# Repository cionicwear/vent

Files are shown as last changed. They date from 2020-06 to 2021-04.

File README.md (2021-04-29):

# vent

Vent is a collaboration between CIONIC and FuseProject to build a highly modular low cost ventilator 
to help address a potential capacity shortfall in emergency COVID-19 response.

Our design is a finalist in the [Covent-19 Challenge](https://www.coventchallenge.com/)

## pi development

The fully featured Vent has been tested to run on [Raspberry Pi 4](https://www.raspberrypi.org/products/raspberry-pi-4-model-b/) 

The headless version has been tested to run on [Raspberry Pi 0](https://www.raspberrypi.org/products/raspberry-pi-zero-w/)

### pi setup

```
git clone https://github.com/cionicwear/vent.git
cd vent
sudo pip3 install -r requirements.txt
```

Vent requires running two i2c busses to configure your pi
Add the following overlay to /boot/config.txt
```
dtoverlay=i2c-gpio,i2c_gpio_sda=4,i2c_gpio_scl=26,bus=3
```

### pi running

There are three different processes that need to be 

1. start the ui process
```
sudo ./ui.py
```
The UI process manages the rotary encoder and buttons translating them to system wide keystrokes

2. start the vent process
```
sudo ./vent.py
```
The vent process is the primary control point that manges the web server, sensors, and valve.

3. start the screen process
```
./vent.sh
```
The chromium browser serves as the surface for operator input and display of sensor values

## desktop development

In order to enable hardware free development the vent can be run locally via docker.
```
git clone https://github.com/cionicwear/vent.git
cd vent
docker-compose up
```

## command line testing

Much of the vent functionality can be tested via the command line.  

```
sudo ./vent.py -h
```

will print out diffrent vent parameters that can be tested

```
usage: vent.py [-h] [-m MODE] [-a ASSIST] [-i INSPIRE] [-e EXPIRE] [-u RAMPUP]
               [-d RAMPDN] [-s START] [-t TOP] [-p PAUSE] [-b BOTTOM]
               [-c COUNT] [-f FIO2] [-v VTIDAL] [-w PWAIT] [-x PCROSS]

Run vent

optional arguments:
  -h, --help            show this help message and exit
  -m MODE, --mode MODE  0 = Demo 1 = Volume Control 2 = Pressure Control
  -a ASSIST, --assist ASSIST
                        pressure trigger for assist 0 = no assist
  -i INSPIRE, --inspire INSPIRE
                        seconds of inspiration time
  -e EXPIRE, --expire EXPIRE
                        seconds of expiration time
  -u RAMPUP, --rampup RAMPUP
                        seconds to ramp from <start> to <top>
  -d RAMPDN, --rampdn RAMPDN
                        seconds to ramp from <top> to <pause>
  -s START, --start START
                        percent open at start of breathing cycle
  -t TOP, --top TOP     percent open at peak of breathing cycle
  -p PAUSE, --pause PAUSE
                        percent open at pause in breathing cycle
  -b BOTTOM, --bottom BOTTOM
                        percent open at end of breathing cycle
  -c COUNT, --count COUNT
                        number of breathing cycles
  -f FIO2, --fio2 FIO2  fio2
  -v VTIDAL, --vtidal VTIDAL
                        tidal volume
  -w PWAIT, --pwait PWAIT
                        seconds to wait before closing peep
  -x PCROSS, --pcross PCROSS
                        peep crossing threshold
```

For example if you wanted to test
 - 1 second of inspire time
 - 90% air flow
 - with a 0.2 second peep time
 - for 10 cycles

You would run the command

```
sudo ./vent.py -c 10 -t 90 -w 0.2 -x 0.1
```

Note: the `-x -1` sets the peep pressure threshold to -1 to set the auto peep to trigger at -1 cmH20.  This is useful when testing the system with no airflow.

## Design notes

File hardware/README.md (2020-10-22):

# Hardware Specifications

There have been two revisions to the hardware reference design

* RevA initial concept
* RevB functional prototype

## RevB Functional Prototype

The RevB reference design made rapid deployment even easier by leveraging off the shelf breakout boards for almost all components.

[Mechanical Assembly](mechanical/RevB.STEP)

[Electrical Schematic](electrical/RevB.pdf)

[Bill of Materials](bom/RevB.csv)

Electronics

- 1x [Raspberry Pi 4](https://www.raspberrypi.org/products/raspberry-pi-4-model-b/) for compute
- 1x [Raspberry Pi Touch Display](https://www.raspberrypi.org/products/raspberry-pi-touch-display/) for UI
- 4x [Adafruit LPS33HW Pressure Sensor](https://www.adafruit.com/product/4414) for measuring pressure and flow
- 1x [Adafruit Motor Bonnet](https://www.adafruit.com/product/4280) for driving solenoids and linear actuator
- 2x [SMC PVQ31-6G-40-01-N Solenoid](https://www.smcpneumatics.com/pdfs/PVQ.pdf) for control of O2 and Room Air
- 1x [Actuonix L12-10-50-12-P Linear Actuator](https://s3.amazonaws.com/actuonix/Actuonix+L12+Datasheet.pdf) for controlling PEEP
- 1x [Sensoronics SS-26 O2 Sensor](https://www.sensoronics.com/products/ss-26-replaces-msa-806572) for O2 Sensing
- 1x [Sparkfun QWIIC ADS1105](https://www.sparkfun.com/products/15334) to read analog O2 and actuator position sensors
- 1x [GOOLOO GP37-plus](http://www.gooloo.com/products-detail.php?ProId=41) for power management and battery backup
- 2x [B3F-1020 Tactile Switch](https://www.digikey.com/product-detail/en/omron-electronics-inc-emc-div/B3F-1020/SW402-ND/44059) for UI
- 1x [PEC11R-4015F-S0024 Rotary Encoder](https://www.digikey.com/product-detail/en/bourns-inc/PEC11R-4015F-S0024/PEC11R-4015F-S0024-ND/4499668) for UI
- 1x [CEM-1203_42 Audio Transducer](https://www.digikey.com/product-detail/en/cui-devices/CEM-1203-42/102-1153-ND/412412) for Alarms

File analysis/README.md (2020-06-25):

## FMEA

The team conducted a [Failure Mode and Effects Analysis](https://github.com/cionicwear/vent/blob/master/analysis/VOX_FMEA.xlsx) to determine areas of risk with this reference design

## Ventilator Mode Testing

Ventilator modes  tested using refrence equipment from AD Instruments and MGH/Ximedica (listed in table below)  
That data was then exported for anlysis vs. system diagnostics generated by the VOX vent  
And compared in Jupyter notebooks [vent.ipynb](analysis/vent.ipynb) to generate pdf reports (linked in table below)

|   Pressure Transducer                                |   ADInstruments   |   Measure the air pressure.                                                     | Tidal Volume ml | Breaths / min (a) | Inspire time (s) | O2 | BAP (PEEP) | I:E |
|------------------------------------------------------|-------------------|---------------------------------------------------------------------------------|-----------------|-------------------|------------------|----|------------|-----|
|   FE221 Bridge Amp                                   |   ADInstruments   |   Sends data from pressure transducer to PowerLab.                              | 500             | 20                | 1                | 30 | 5          | 1:2 |
|   Cables                                             |   ADInstruments   |   Used to connect amp to PowerLab.                                              | 500             | 12                | 1                | 90 | 10         | 1:4 |
|   MLT1000 Flow Head                                  |   ADInstruments   |   Used to measure air flow.                                                     | 500             | 20                | 1                | 90 | 5          | 1:2 |
|   Flow Head Tubing                                   |   ADInstruments   |   Connects between flow head and spirometer.                                    | 500             | 20                | 1                | 30 | 10         |     |
|   ML311 Spirometer Pod                               |   ADInstruments   |   Measures the flow rate of air for other calculations.                         | 300             | 20                | 1                | 30 | 5          |     |
|   PowerLab                                           |   ADInstruments   |   Collects data and sends to LabChart.                                          | 300             | 12                | 1                | 90 | 10         | 1:3 |
|   LabChart License                                   |   ADInstruments   |   Used to collect, display, and analyze data.                                   | 300             | 20                | 1                | 30 | 10         |     |
|   IngMar Medical QuickLung Test Lung or Equivalent   |   MGH/Ximedica    |   Has adjustable resistance and compliance to help simulate a person’s lungs.   | 200             | 20                | 1                | 90 | 5          |     |

### Pressure Control Testing

|   | Compliance ml/hPa ±10%                                                       | Resistance  hPa/l/s ±10% | Tidal Volume ml (a) | Breaths / min (b) | Inspire time (s) (c) | O2 | BAP (PEEP) | Δ insp pressure (d) |
|---|------------------------------------------------------------------------------|--------------------------|---------------------|-------------------|----------------------|----|------------|---------------------|
| [ISO_PCV1](ISO_PCV1.pdf) | 50.                                                            | 5                        | 500                 | 20                | 1                    | 30 | 5          | 10                  |
| [ISO_PCV2](ISO_PCV2.pdf) | 50                                                                           | 20                       | 500                 | 12                | 1                    | 90 | 10         | 15                  |                                     |
| ISO_PCV3 | 20                                                                           | 5                        | 500                 | 20                | 1                    | 90 | 5          | 25                  |

### Volume Control Testing

|      | Compliance ml/hPa ±10% | Resistance  hPa/l/s ±10% | Tidal Volume ml | Breaths / min (a) | Inspire time (s) | O2 | BAP (PEEP) | I:E |
|------|------------------------|--------------------------|-----------------|-------------------|------------------|----|------------|-----|
| [ISO1](ISO1.pdf)    | 50                     | 5                        | 500             | 20                | 1                | 30 | 5          | 1:2 |
| [ISO2](ISO2.pdf)   | 50                     | 20                       | 500             | 12                | 1                | 90 | 10         | 1:4 |
| [ISO3](ISO3.pdf)   | 20                     | 5                        | 500             | 20                | 1                | 90 | 5          | 1:2 |
| 4    | 20                     | 20                       | 500             | 20                | 1                | 30 | 10         |     |
| 5    | 20                     | 20                       | 300             | 20                | 1                | 30 | 5          |     |
| 6    | 20                     | 50                       | 300             | 12                | 1                | 90 | 10         | 1:3 |
| 7    | 10                     | 50                       | 300             | 20                | 1                | 30 | 10         |     |
| 8    | 10                     | 10                       | 200             | 20                | 1                | 90 | 5          |     |
| [C200](C200.pdf)  | 50                     | 5                        | 200             | 15                | 1                | 20 | 5          | 1:3 |
| C300 | 50                     | 5                        | 300             | 15                | 1                | 20 | 5          | 1:3 |
| C400 | 50                     | 5                        | 400             | 15                | 1                | 20 | 5          | 1:3 |
| C500 | 50                     | 5                        | 500             | 15                | 1                | 20 | 5          | 1:3 |
| C600 | 50                     | 5                        | 600             | 15                | 1                | 20 | 5          | 1:3 |
| [P15](P15.pdf)  | 50                     | 5                        | 500             | 10                | 1                | 20 | 15         | 1:5 |
| [R30](R30.pdf)  | 50                     | 5                        | 200             | 30                | 1                | 20 | 5          | 1:1 |

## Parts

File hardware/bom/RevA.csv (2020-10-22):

QTY | Description | P/N
6 | SCREW M3 x 5mm BH TORX | 92832A214
1 | RELIEF VALVE | 48935K250
2 | VENTURI TUBE ELBOW ADAPTER | PRINTED
1 | VENTURI TUBE EXHALE | PRINTED
1 | BARREL JACK 2.1mm DC | 610 ADAFRUIT
1 | COVER PANEL REAR | MACHINED
6 | SCREW M5 x 8mm PH TORX | 90304A218
8 | SCREW M4 x 8mm FH THREAD FORMING | STP41040-0080
1 | O2 SENSOR | SS-26
1 | VENTURI TUBE ADAPTER | PRINTED
1 | VENTURI TUBE INHALE | PRINTED
1 | ROTARY ENCODER | PEC11R-4015F-S0024
1 | POWER BUTTON | IPR1SAD2
1 | ENCLOSURE | PRINTED
4 | SCREW M3 x 12mm PH THREAD FORMING | 96817A912
2 | QUICK DISCONNECT AIR CONNECT ADAPTER | 5012K320
1 | HIGH-PURITY POLYPROPYLENE TUBING 0.25 INCH OD | 4218N11
1 | HIGH-PURITY POLYPROPYLENE TUBING 0.25 INCH OD | 4218N11
1 | HIGH-PURITY POLYPROPYLENE TUBING 0.25 INCH OD | 4218N11
1 | HIGH-PURITY POLYPROPYLENE TUBING 0.25 INCH OD | 4218N11
1 | HIGH-PURITY POLYPROPYLENE TUBING 0.25 INCH OD | 4218N11
1 | HIGH-PURITY POLYPROPYLENE TUBING 0.25 INCH OD | 4218N11
1 | HIGH-PURITY POLYPROPYLENE TUBING 0.25 INCH OD | 4218N11
1 | HIGH-PURITY POLYPROPYLENE TUBING 0.25 INCH OD | 4218N11
1 | HIGH-PURITY POLYPROPYLENE TUBING 0.25 INCH OD | 4218N11
1 | HIGH-PURITY POLYPROPYLENE TUBING 0.25 INCH OD | 4218N11
1 | HIGH-PURITY POLYPROPYLENE TUBING 0.25 INCH OD | 4218N11
1 | SUB-ASSY VALVE PLATE | 3D printed
3 | FITTING AIR MALE-PUSH CONNECT 0.125 INCH NPT | KQ2H07-34N
1 | RASPBERRY PI 4 MODEL B | RPI4B
6 | SCREW M2.63 x 5mm RH TORX THREAD FORMING | 99397A413
1 | HIGH-PURITY HARD POLYPROPYLENE TUBING | 4218N11
4 | FITTING AIR MALE-PUSH CONNECT 0.25 INCH NPT | KQ2H07-35N
3 | PROPORTIONAL SOLENOID VALVE | PVQ31-6G-16-01-F
2 | METRIC THREAD-FORMING SCREW FOR PLASTIC | 99397A679
1 | REGULATOR BRACKET | -
1 | PUSH-CONNECT BRANCH TEE TUBING ADAPTER | KQ2T07-34AS
1 | HIGH-PURITY HARD POLYPROPYLENE TUBING | 4218N11
2 | NONADJUSTABLE MINIATURE AIR WATER REGULATOR | 9386K410
2 | CHECK VALVE | AKH07B-N01S
1 | SENSOR BOARD PCBA | -
2 | DIFFERENTIAL PRESSURE SENSOR | D6F_P0010A2
1 | SENSOR BOARD PCB | -
2 | PRESURE SENSOR GAUGE | P-2000-501G-15-BN
4 | SCREW M2.63 x 8mm RH TORX THREAD FORMING | 99397A415
1 | HIGH-PURITY HARD POLYPROPYLENE TUBING | 4218N11
1 | PLATE ABS VALVE MOUNTING | -
1 | BRACKET CABLE MANAGEMENT | -
1 | PEEP VALVE | -
1 | SUB-ASSY FRONT PLATE | MACHINED
1 | COVER PANEL FRONT | MACHINED
6 | STAINLESS STEEL STAND-OFF | CSS-M3-12
1 | SUB-ASSY DISPLAY | -
10 | SCREW M2.63 x 8mm RH TORX THREAD FORMING | 99397A415
1 | DISPLAY MOUNT | PRINTED
1 | RASPBERRY PI 7IN LCD | 8997466
1 | BUTTON PCBA | -
2 | TACTILE SWITCH SPST-NO | B3F-1020
1 | MAGNETIC BUZZER TRANSDUCER | CEM-1203_42
1 | BUTTON PCB | -
4 | SCREW M3 x 5mm PH PHILLIPS | 90116A150
2 | BUTTON COVER COSMETIC | PRINTED
1 | PI DISPLAY PCBA | -
3 | IV POLE C-CLAMP | BK-IVP-8950
1 | TUBE GUIDE PATIENT CIRCUIT | -
1 | Quad Low-Side Solenoid Driver | DRV8803
1 | Power Management IC | TPS259571DSGR
1 | Analog to Digital Converter | ADS1115IDGSR

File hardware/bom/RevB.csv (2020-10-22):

QTY | Description | P/N
PRINTED
1 | ENCLOSURE | PRINTED
1 | LINEAR ACTUATOR MOUNT | PRINTED
1 | VALVE MOUNTING PLATE | PRINTED
1 | BRACKET CABLE MANAGEMENT | PRINTED
1 | DISPLAY MOUNT | PRINTED
1 | VENTURI INSPIRATION | PRINTED
1 | VENTURI EXPIRATION | PRINTED
2 | BUTTON COVER COSMETIC | PRINTED
1 | ROTARY ENCODER COVER COSMETIC | PRINTED
1 | LINEAR ACTUATOR PEEP CAP | PRINTED
1 | OXYGEN SENSOR MOUNT | PRINTED
MACHINED
1 | FRONT COVER PANEL WITH STANDOFFS | MACHINED
1 | TUBE GUIDE PATIENT CIRCUIT | MACHINED
1 | REAR COVER PANEL | MACHINED
ELECTRONICS
1 | OXYGEN SENSOR | SENSORONICS SS26
2 | PROPORTIONAL SOLENOID VALVE | SMC PVQ31-6G-40-01N
1 | LINEAR ACTUATOR | ACTUONIX L12-10-50-12-P
1 | RASPBERRY PI 7IN LCD | DIGIKEY 1690-1007-ND
1 | RASPBERRY PI 4 MODEL B | DIGIKEY 1690-RASPBERRYPI4B/2GB-ND
1 | ADAFRUIT MOTOR BONNET 4280 | DIGIKEY 1528-4280-ND
4 | PRESSURE SENSOR LPS33HW BREAKOUT 4414 | DIGIKEY 1528-4414-ND
1 | BATTERY BACKUP | GOOLOO GP37+
1 | MAGNETIC BUZZER TRANSDUCER CEM-1203(42) | DIGIKEY 102-1153-ND
2 | TACTILE SWITCH B3F-1020 | DIGIKEY SW402-ND
1 | ADAFRUIT PANEL MOUNT BARREL JACK 2.1mm DC | ADAFRUIT 610
1 | ROTARY ENCODER | DIGIKEY PEC11R-4015F-S0024-ND
1 | PANEL MOUNT POWER BUTTON IPR1SAD2 | DIGIKEY 679-1099-ND
1 | SPARKFUN QWIIC ADS1015 BREAKOUT | DIGIKEY 1568-DEV-15334-ND
1 | BUTTON PCBA | HAND SOLDERED
OTHER
3 | IV POLE C-CLAMP | BK-IVP-8950
1 | 70A BUNA N 001-1/2 O RING (100 pack) | MCMASTER 9452K311
2 | QUICK DISCONNECT AIR CONNECT ADAPTER | MCMASTER 5012K44
2 | QUICK DISCONNECT AIR CONNECT ADAPTER | MCMASTER 5012K34
1 | HIGH-PURITY POLYPROPYLENE TUBING 1/4 IN OD | MCMASTER 4218N11
1 | HIGH-PURITY POLYPROPYLENE TUBING 3/8 IN OD | MCMASTER 4218N12
1 | PUSH TO CONNECT WYE 3/8 IN OD | MCMASTER 5779K46
5 | PUSH TO CONNECT TUBE FITTING 3/8 IN OD 1/8 NPT | MCMASTER 5779K115
2 | PUSH TO CONNECT TUBE FITTING 1/4 IN OD 1/8 NPT | MCMASTER 5779K108
1 | PRESSURE RELIEF VALVE | 48935K250
10 | SCREW M2.63 x 8mm RH TORX THREAD FORMING | 99397A415
4 | SCREW M3 x 5mm PH PHILLIPS | 90116A150
6 | SCREW M2.63 x 5mm RH TORX THREAD FORMING | 99397A413
4 | SCREW M3 x 12mm PH THREAD FORMING | 96817A912
6 | SCREW M5 x 8mm PH TORX | 90304A218
8 | SCREW M4 x 8mm FH THREAD FORMING | STP41040-0080
1 | LINEAR ACTUATOR PEEP CAP PADDING | TBD

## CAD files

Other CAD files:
hardware/mechanical/RevA.STEP
hardware/mechanical/RevB.STEP

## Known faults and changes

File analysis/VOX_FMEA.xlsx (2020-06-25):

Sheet: FMEA
Product/Process | InVent Ventilator | Date Created | 2020-05-08
Prepared By | Jonathan Schreven & Eric Spaulding
Notes | Last updated on 5/11/2020 by Jonathan Schreven
Function / Requirement | Potential failure mode | Potential effect of failure | SEV | Class | Current process controls |  |  |  |  |  | Recommended actions |  |  | Action results
 |  |  |  |  | Potential cause | Occur | Prevention | Detection | Det | R.P.N. | Recommended actions | Responsible | Target completion date | Actions Taken | Sev | Occur | Det | R.P.N. | Class
O2 Inlet Fitting | Air supply line connected | Incorrect FiO2 delivery to patient | 8 |  | User error | 5 | None | Visual inspection, FiO2 alarm | 5 | 200 |  |  |  |  |  |  |  | 0
 | External O2 line disconnects | Incorrect/insufficient O2 delivery to patient | 6 |  | Connector breaks | 1 | Locking connector | Visual inspection | 2 | 12 |  |  |  |  |  |  |  | 0
 | Internal tubing disconnects | Incorrect/insufficient O2 delivery to patient | 6 |  | Tube slips off fitting | 1 | Multi-barbed fitting | Audible gas leak | 2 | 12 |  |  |  |  |  |  |  | 0
 | Insufficient inlet pressure | Insufficient outlet pressure to drive patient breath | 5 |  | Tank empty or nearly empty | 8 | None | FiO2 alarm | 2 | 80 |  |  |  |  |  |  |  | 0
 |  |  |  |  | Incorrect O2 tank pressure setting | 8 | None | FiO2 alarm | 3 | 120 |  |  |  |  |  |  |  | 0
 |  |  |  |  |  |  |  |  |  | 0 |  |  |  |  |  |  |  | 0
O2 Inlet Pressure Regulator | Pressure setting too low | Incorrect FiO2 delivery to patient | 5 |  | Manufacturer quality control issue | 1 | None | FiO2 alarm | 1 | 5 |  |  |  |  |  |  |  | 0
 | Pressure setting too high | Damage air mixing tank structure | 5 |  | Manufacturer quality control issue | 1 | None | FiO2 Alarm, Audible gas leak | 7 | 35 |  |  |  |  |  |  |  | 0
 | Tubing disconnect | Incorrect FiO2 delivery to patient | 6 |  | Improper assembly | 2 | None | FiO2 Alarm, Audible gas leak | 2 | 24 |  |  |  |  |  |  |  | 0
 |  |  |  |  |  |  |  |  |  | 0 |  |  |  |  |  |  |  | 0
O2 Inlet Solenoid | Power Failure | N.C. Valve - Oxygen line turns off | 6 |  | Power cord removed from wall/unit | 3 | Cable management | Visual inspection | 1 | 18 |  |  |  |  |  |  |  | 0
 |  |  |  |  | Bump power switch | 5 | Flush button on rear of unit | Visual inspection | 3 | 90 |  |  |  |  |  |  |  | 0
 | Tubing disconnect | Incorrect FiO2 delivery to patient | 6 |  | Improper assembly | 2 | None | Audible gas leak, FiO2 alarm | 2 | 24 |  |  |  |  |  |  |  | 0
 | Seal fails | Incorrect FiO2 delivery to patient | 5 |  | Manufacturer defect | 1 | None | Audible gas leak, FiO2 alarm | 3 | 15 |  |  |  |  |  |  |  | 0
 |  |  |  |  |  |  |  |  |  | 0 |  |  |  |  |  |  |  | 0
Air Inlet Fitting | O2 supply line connected | Incorrect FiO2 delivery to patient | 8 |  | User error | 5 | None | Visual inspection, FiO2 alarm | 5 | 200 |  |  |  |  |  |  |  | 0
 | External Air line disconnects | Incorrect/insufficient O2 delivery to patient | 8 |  | Connector breaks | 1 | Locking connector | Visual inspection | 2 | 16 |  |  |  |  |  |  |  | 0
 | Internal tubing disconnects | Incorrect/insufficient O2 delivery to patient | 8 |  | Tube slips off fitting | 1 | Barbed fitting | Audible gas leak | 2 | 16 |  |  |  |  |  |  |  | 0
 | Insufficient inlet pressure | Insufficient outlet pressure to drive patient breath | 5 |  | Tank empty or nearly empty | 8 | None | FiO2 alarm | 2 | 80 |  |  |  |  |  |  |  | 0
 |  |  |  |  | Incorrect O2 tank pressure setting | 8 | None | FiO2 alarm | 3 | 120 |  |  |  |  |  |  |  | 0
 |  |  |  |  |  |  |  |  |  | 0 |  |  |  |  |  |  |  | 0
Air Inlet Pressure Regulator | Pressure setting too low | Incorrect FiO2 delivery to patient | 5 |  | Manufacturer quality control issue | 1 | None | FiO2 alarm | 1 | 5 |  |  |  |  |  |  |  | 0
 | Pressure setting too high | Damage air mixing tank | 5 |  | Manufacturer quality control issue | 1 | None | FiO2 Alarm, Audible gas leak | 7 | 35 |  |  |  |  |  |  |  | 0
 | Tubing disconnect | Incorrect FiO2 delivery to patient | 8 |  | Improper assembly | 2 | None | FiO2 Alarm, Audible gas leak | 2 | 32 |  |  |  |  |  |  |  | 0
 |  |  |  |  |  |  |  |  |  | 0 |  |  |  |  |  |  |  | 0
Air Inlet Solenoid | Power Failure | N.C. Valve - Air line turns off | 8 |  | Power cord removed from wall/unit | 3 | Cable management | Visual inspection | 1 | 24 |  |  |  |  |  |  |  | 0
 |  |  |  |  | Bump power switch | 5 | Flush button on rear of unit | Visual inspection | 3 | 120 |  |  |  |  |  |  |  | 0
 | Tubing disconnect | Incorrect FiO2 delivery to patient | 8 |  | Improper assembly | 2 | None | Audible gas leak, FiO2 alarm | 2 | 32 |  |  |  |  |  |  |  | 0
 | Seal fails | Incorrect FiO2 delivery to patient | 7 |  | Manufacturer defect | 1 | None | Audible gas leak, FiO2 alarm | 3 | 21 |  |  |  |  |  |  |  | 0
 |  |  |  |  |  |  |  |  |  | 0 |  |  |  |  |  |  |  | 0
Gas Mixing Tank | Hose barb breaks | No gas delivery to patient | 9 |  | Fatigue from hose movement | 3 | Functional prototype cycle testing | Audible gas leak, FiO2 alarm | 2 | 54 |  |  |  |  |  |  |  | 0
 | Tank damage | No gas to patient | 10 |  | Over pressure | 2 | FEA Analysis, SF = 3 | Audible gas leak, FiO2 alarm | 2 | 40 |  |  |  |  |  |  |  | 0
 | Tank gasket fails | Insufficient outlet pressure to drive patient breath | 8 |  | Assembly error | 3 | Pressure check at manufacturing | Audible gas leak, FiO2 alarm | 3 | 72 |  |  |  |  |  |  |  | 0
 |  |  |  |  | System Overpressure | 1 | Upstream pressure regulators | Audible gas leak, FiO2 alarm | 3 | 24 |  |  |  |  |  |  |  | 0
 | Tubing disconnect | No gas to patient | 9 |  | Tube slips off fitting | 2 | Barbed fitting | Audible gas leak | 3 | 54 |  |  |  |  |  |  |  | 0
 |  |  |  |  |  |  |  |  |  | 0 |  |  |  |  |  |  |  | 0
Gas Outlet Solenoid | Power Failure | N.C. Valve - No gas to patient | 9 |  | Power cord removed from wall/unit | 3 | Cable management | Visual inspection | 1 | 27 |  |  |  |  |  |  |  | 0
 |  |  |  |  | Bump power switch | 5 | Flush button on rear of unit | Visual inspection | 3 | 135 |  |  |  |  |  |  |  | 0
 | Tubing disconnect | Incorrect FiO2 delivery to patient | 9 |  | Improper assembly | 2 | None | Audible gas leak, FiO2 alarm | 2 | 36 |  |  |  |  |  |  |  | 0
 | Seal fails | Incorrect FiO2 delivery to patient | 7 |  | Manufacturer defect | 1 | None | Audible gas leak, FiO2 alarm | 3 | 21 |  |  |  |  |  |  |  | 0
 | Valve sticks open | Excessive pressure delivered to patient | 9 |  | Mechanical valve failure | 2 | Emergency pressure relief valve | PIP monitor | 1 | 18 |  |  |  |  |  |  |  | 0
 |  |  |  |  | Erroneous control system signal | 2 | System testing, emergency pressure relief valve | PIP monitor | 1 | 18 |  |  |  |  |  |  |  | 0
 | Valve doesn't open enough | Insufficient air volume/flow rate to patient | 8 |  | Erroneous control system signal | 2 | System testing | Tidal Volume not achieved alarm | 1 | 16 |  |  |  |  |  |  |  | 0
 |  |  |  |  |  |  |  |  |  | 0 |  |  |  |  |  |  |  | 0
Inspiratory Flow Sensor (Venturi) | Sensor tubing disconnects | Incorrect gas delivery to patient | 9 |  | Improper assembly | 2 | Pressure check at manufacturing | Tidal Volume not achieved alarm | 3 | 54 | System pause for suspected sensor failure |  |  |  |  |  |  | 0
 | Hose disconnects | No gas delivery to patient | 9 |  | Tube slips off fitting | 2 | Barbed fitting | Audible gas leak | 3 | 54 |  |  |  |  |  |  |  | 0
 | Inlet hose barb breaks | No gas delivery to patient | 9 |  | Fatigue from hose movement | 3 | Functional prototype cycle testing | Audible gas leak, FiO2 alarm | 2 | 54 |  |  |  |  |  |  |  | 0
 | Sensor barb breaks | Incorrect tidal volume to patient | 10 |  | Fatigue from hose movement | 3 | Functional prototype cycle testing | Audible gas leak, FiO2 alarm | 2 | 60 | NPT barbs? |  |  |  |  |  |  | 0
 | Incorrect flow measure | Incorrect tidal volume to patient | 10 |  | Differential pressure sensor malfunction | 2 | Testing against calibrated flow sensor | Tidal volume not achieved alarm | 2 | 40 |  |  |  |  |  |  |  | 0
 | Incorrect pressure measurement | Excess pressure to patient | 9 |  | Pressure sensor malfunction | 2 | None | Insp. Pressure not achieved alarm | 4 | 72 |  |  |  |  |  |  |  | 0
 | Incorrect pressure measurement | Insufficient pressure to patient | 9 |  | Pressure sensor malfunction | 2 | None | Insp. Pressure not achieved alarm | 4 | 72 |  |  |  |  |  |  |  | 0
 |  |  |  |  |  |  |  |  |  | 0 |  |  |  |  |  |  |  | 0
Inspiratory Hose Connection | Hose disconnects | No delivery to paitient | 9 |  | Hose gets caught on something/someone | 3 | Designed to ISO standard, vertical port orientation | External patient sensors (e.g. pulse ox.) | 5 | 135 |  |  |  |  |  |  |  | 0
 | Connection breaks | Incorrect patient gas delivery | 9 |  | Unit dropped | 2 | Designed to ISO standard, port protected behind display | Insp. Pressure and Tidal volume not achieved alarms | 4 | 72 |  |  |  |  |  |  |  | 0
 |  |  |  |  |  |  |  |  |  | 0 |  |  |  |  |  |  |  | 0
Expiratory Hose Connection | Hose disconnects | Incorrect expiratory pressure | 8 |  | Hose gets caught on something/someone | 3 | Designed to ISO standard, vertical port orientation | External patient sensors (e.g. pulse ox.) | 5 | 120 |  |  |  |  |  |  |  | 0
 | Connection breaks | Incorrect patient gas delivery | 8 |  | Unit dropped | 2 | Designed to ISO standard, port protected behind display | Insp. Pressure and Tidal volume not achieved alarms | 4 | 64 |  |  |  |  |  |  |  | 0
 |  |  |  |  |  |  |  |  |  | 0 |  |  |  |  |  |  |  | 0
Expiratory Flow Sensor (Venturi) | Sensor tubing disconnects | Sensors produce false data | 8 |  | Improper assembly | 2 | Pressure check at manufacturing | Tidal Volume not achieved alarm | 3 | 48 |  |  |  |  |  |  |  | 0
 | Hose disconnects | Unable to measure expiratory flow and pressure | 8 |  | Tube slips off fitting | 2 | Barbed fitting | Audible gas leak | 3 | 48 |  |  |  |  |  |  |  | 0
 | Incorrect flow measure | Incorrect measure of patient breating status | 6 |  | Differential pressure sensor malfunction | 2 | Testing against calibrated flow sensor | Tidal volume not achieved alarm | 2 | 24 |  |  |  |  |  |  |  | 0
 | Incorrect PEEP measurement | Incorrect data output | 4 |  | Pressure sensor malfunction | 2 | None | Insp. Pressure not achieved alarm | 4 | 32 |  |  |  |  |  |  |  | 0
 |  |  |  |  |  |  |  |  |  | 0 |  |  |  |  |  |  |  | 0
Unit Mounting | Ventilator slides down IV pole | Patient circuit and/or power disconnect | 9 |  | Pole clamps not tightened enough | 2 | None | Visual observation | 4 | 72 |  |  |  |  |  |  |  | 0
 |  |  |  |  | Bolt loosens due to vibration while moving | 2 | None | Visual observation | 4 | 72 |  |  |  |  |  |  |  | 0
 |  |  |  |  |  |  |  |  |  | 0 |  |  |  |  |  |  |  | 0
Oxygen Sensor | Sensor Failure | Incorrect FiO2 delivery to patient | 9 |  | Fails with normal reading | 2 | None | None | 10 | 180 |  |  |  |  |  |  |  | 0
 |  |  |  |  | Fails with extreme value | 2 | None | Insp. Pressure not achieved or overpressure alarm | 2 | 36 |  |  |  |  |  |  |  | 0
 | Oring failure | Insufficient outlet pressure to drive patient breath | 8 |  | Over compression of o-ring | 2 | None | Audible gas leak, tidal volume and insp. Pressure not achieved alarms | 2 | 32 |  |  |  |  |  |  |  | 0
 | Incorrect characterization of FiO2 in tank | Incorrect FiO2 delivery to patient | 10 |  | Incorrect tank mixing properties | 4 | Testing against calibrated O2 sensor | Visual observation of patient by care taker | 8 | 320 |  |  |  |  |  |  |  | 0
 |  |  |  |  |  |  |  |  |  | 0 |  |  |  |  |  |  |  | 0
 |  |  |  |  |  |  |  |  |  | 0 |  |  |  |  |  |  |  | 0
 |  |  |  |  |  |  |  |  |  | 0 |  |  |  |  |  |  |  | 0
 |  |  |  |  |  |  |  |  |  | 0 |  |  |  |  |  |  |  | 0
 |  |  |  |  |  |  |  |  |  | 0 |  |  |  |  |  |  |  | 0
 |  |  |  |  |  |  |  |  |  | 0 |  |  |  |  |  |  |  | 0
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

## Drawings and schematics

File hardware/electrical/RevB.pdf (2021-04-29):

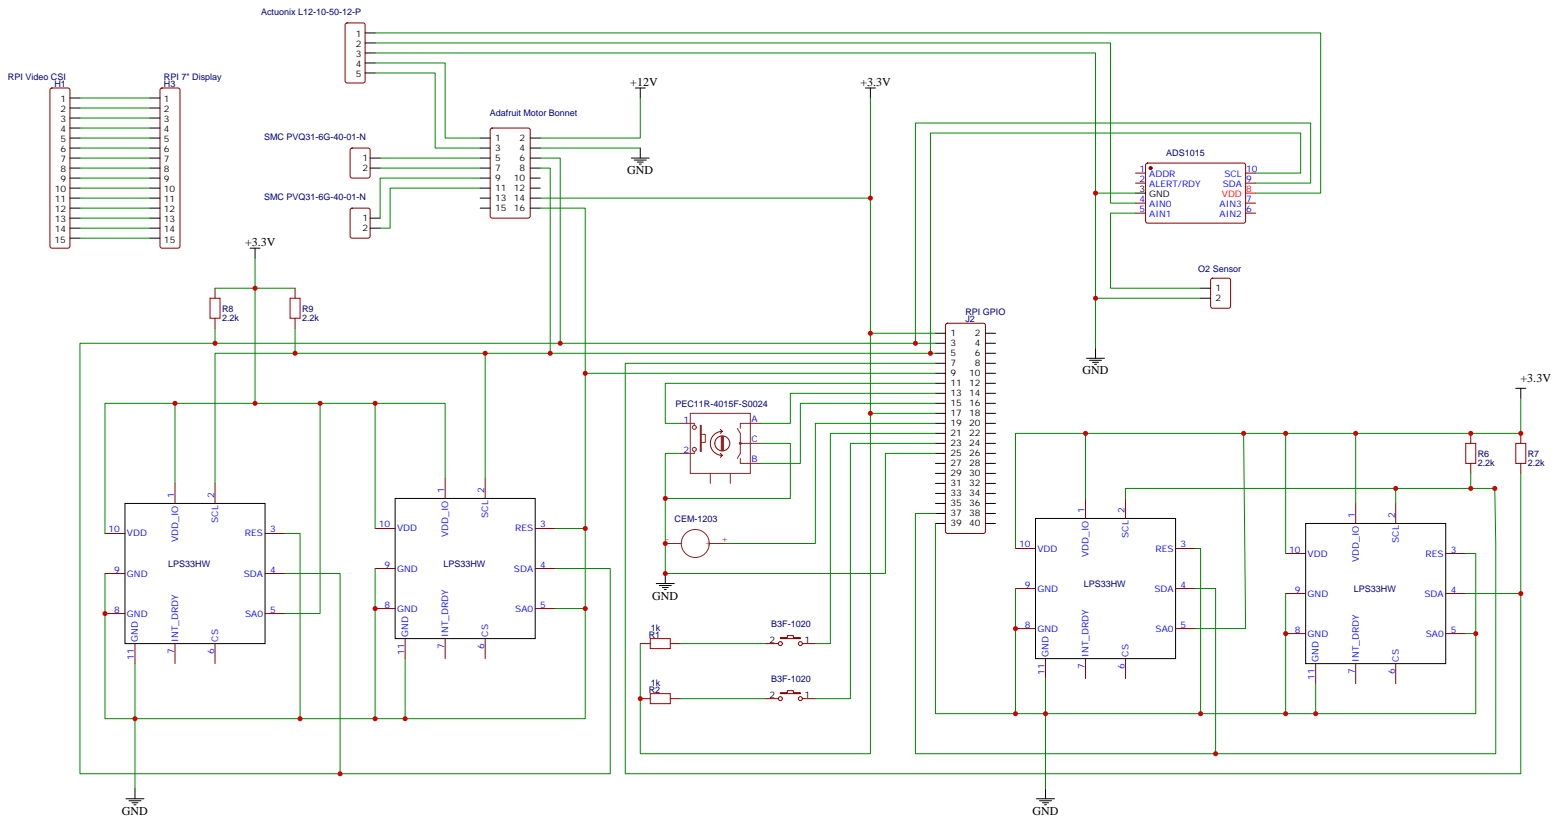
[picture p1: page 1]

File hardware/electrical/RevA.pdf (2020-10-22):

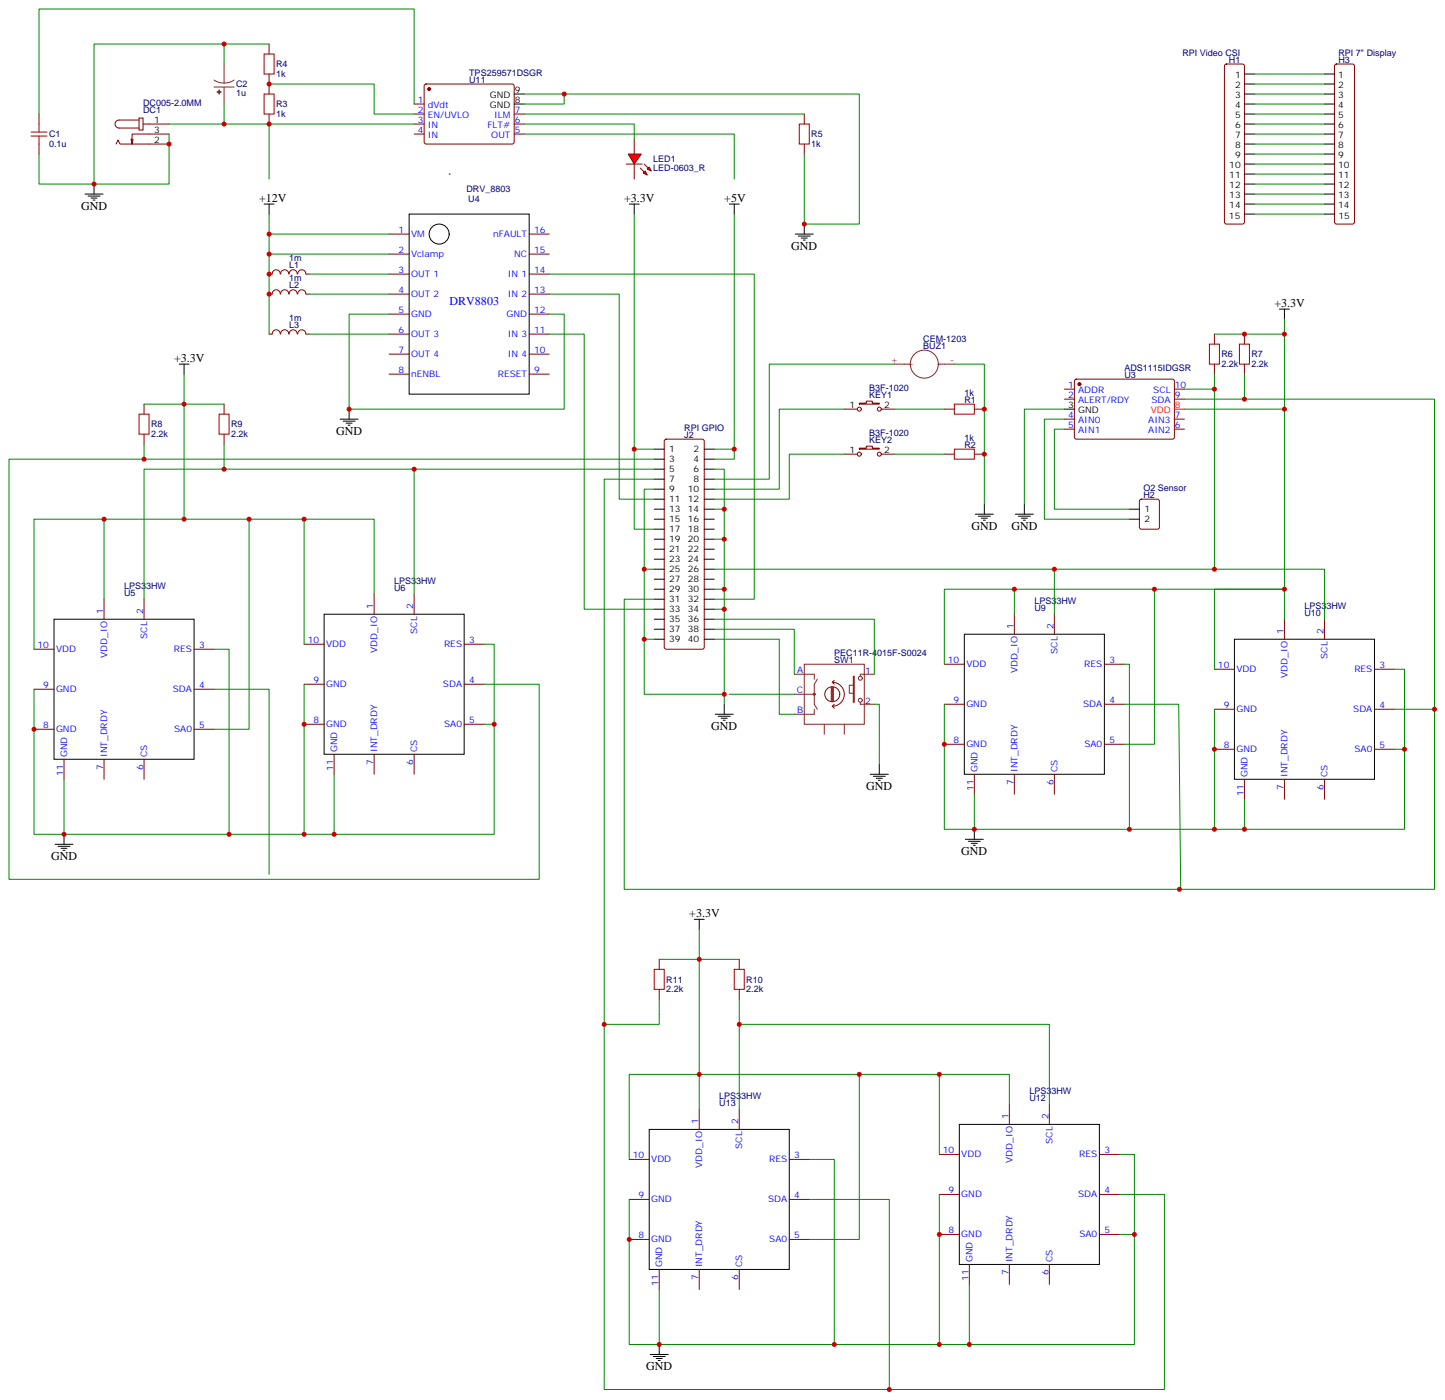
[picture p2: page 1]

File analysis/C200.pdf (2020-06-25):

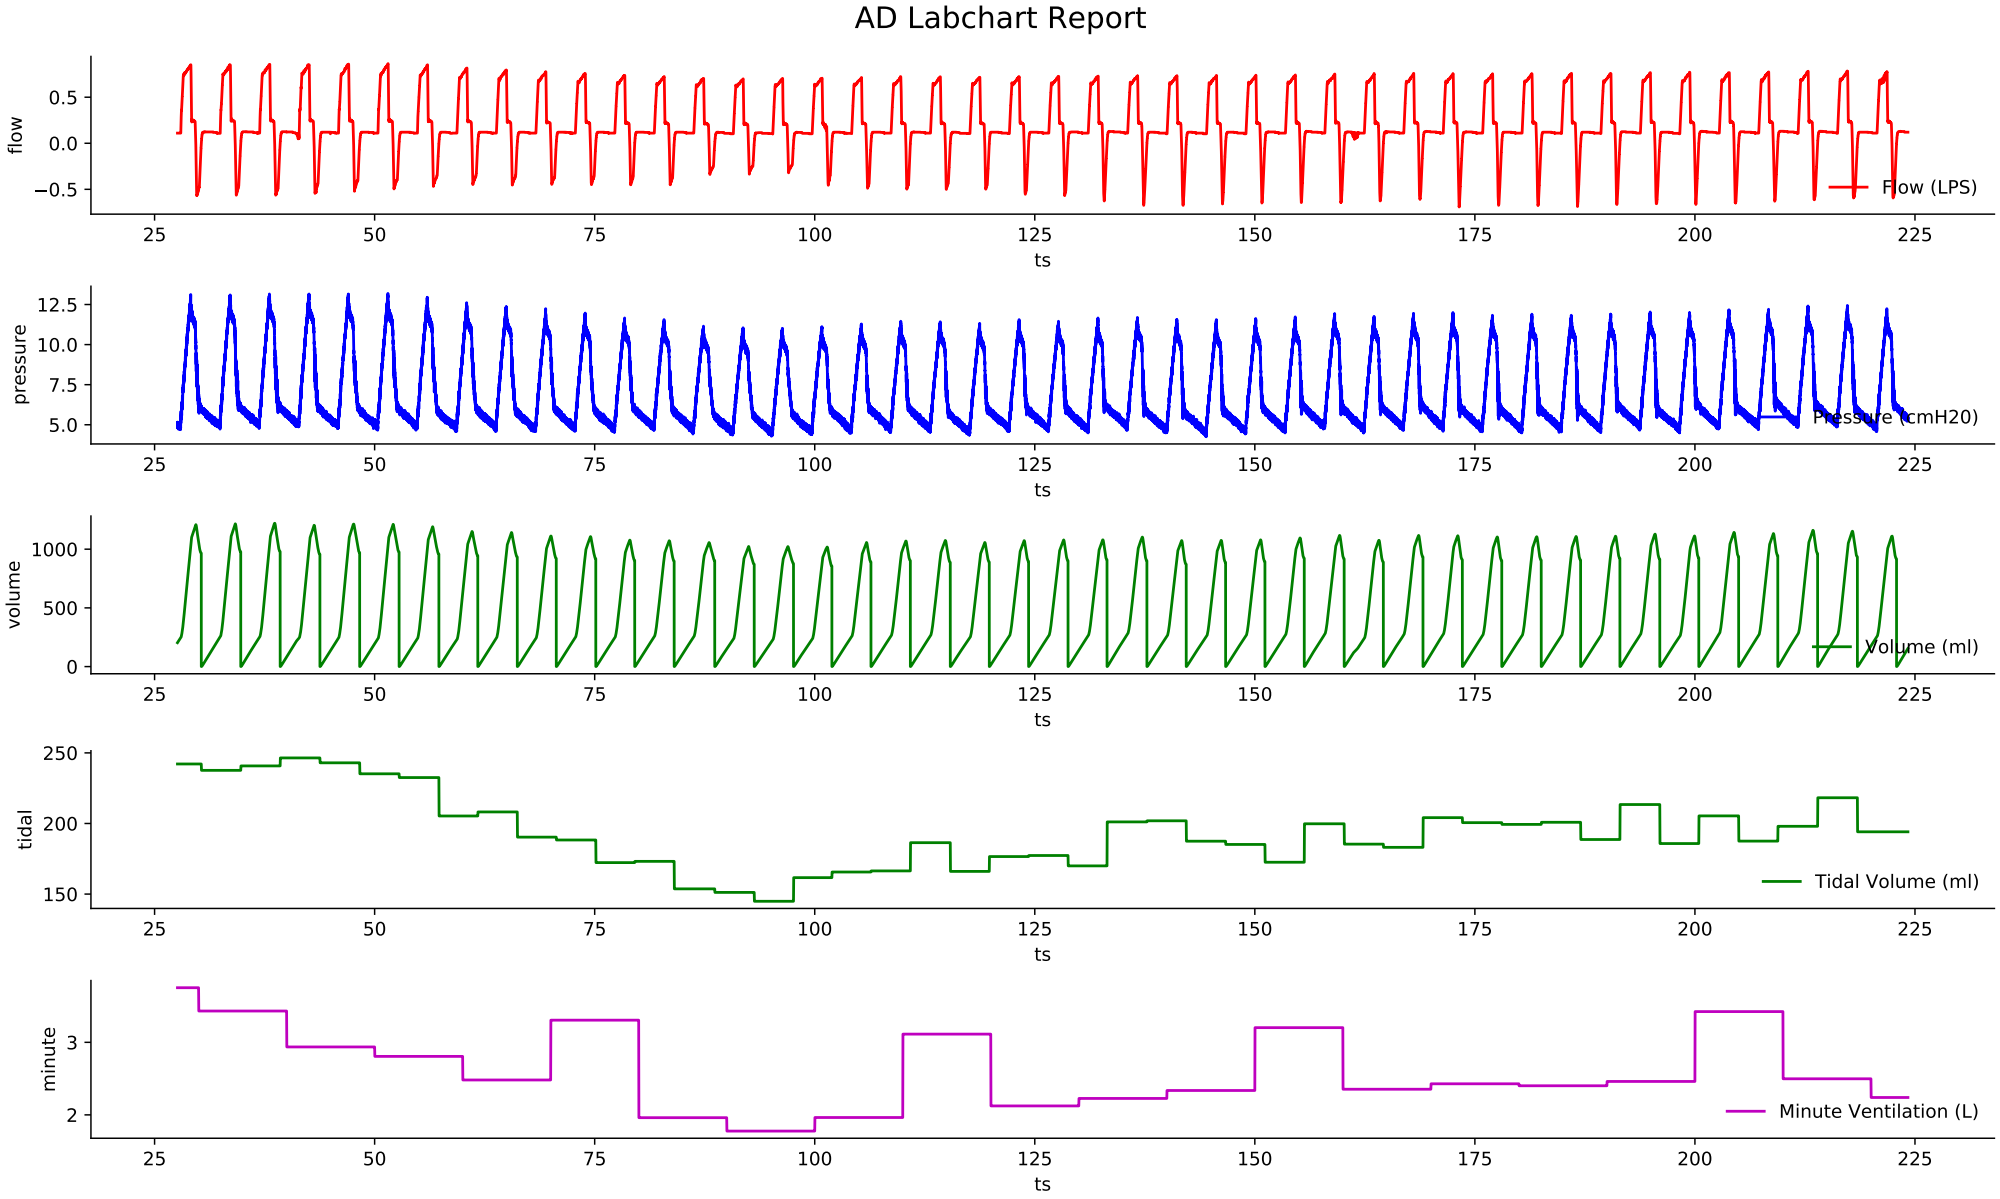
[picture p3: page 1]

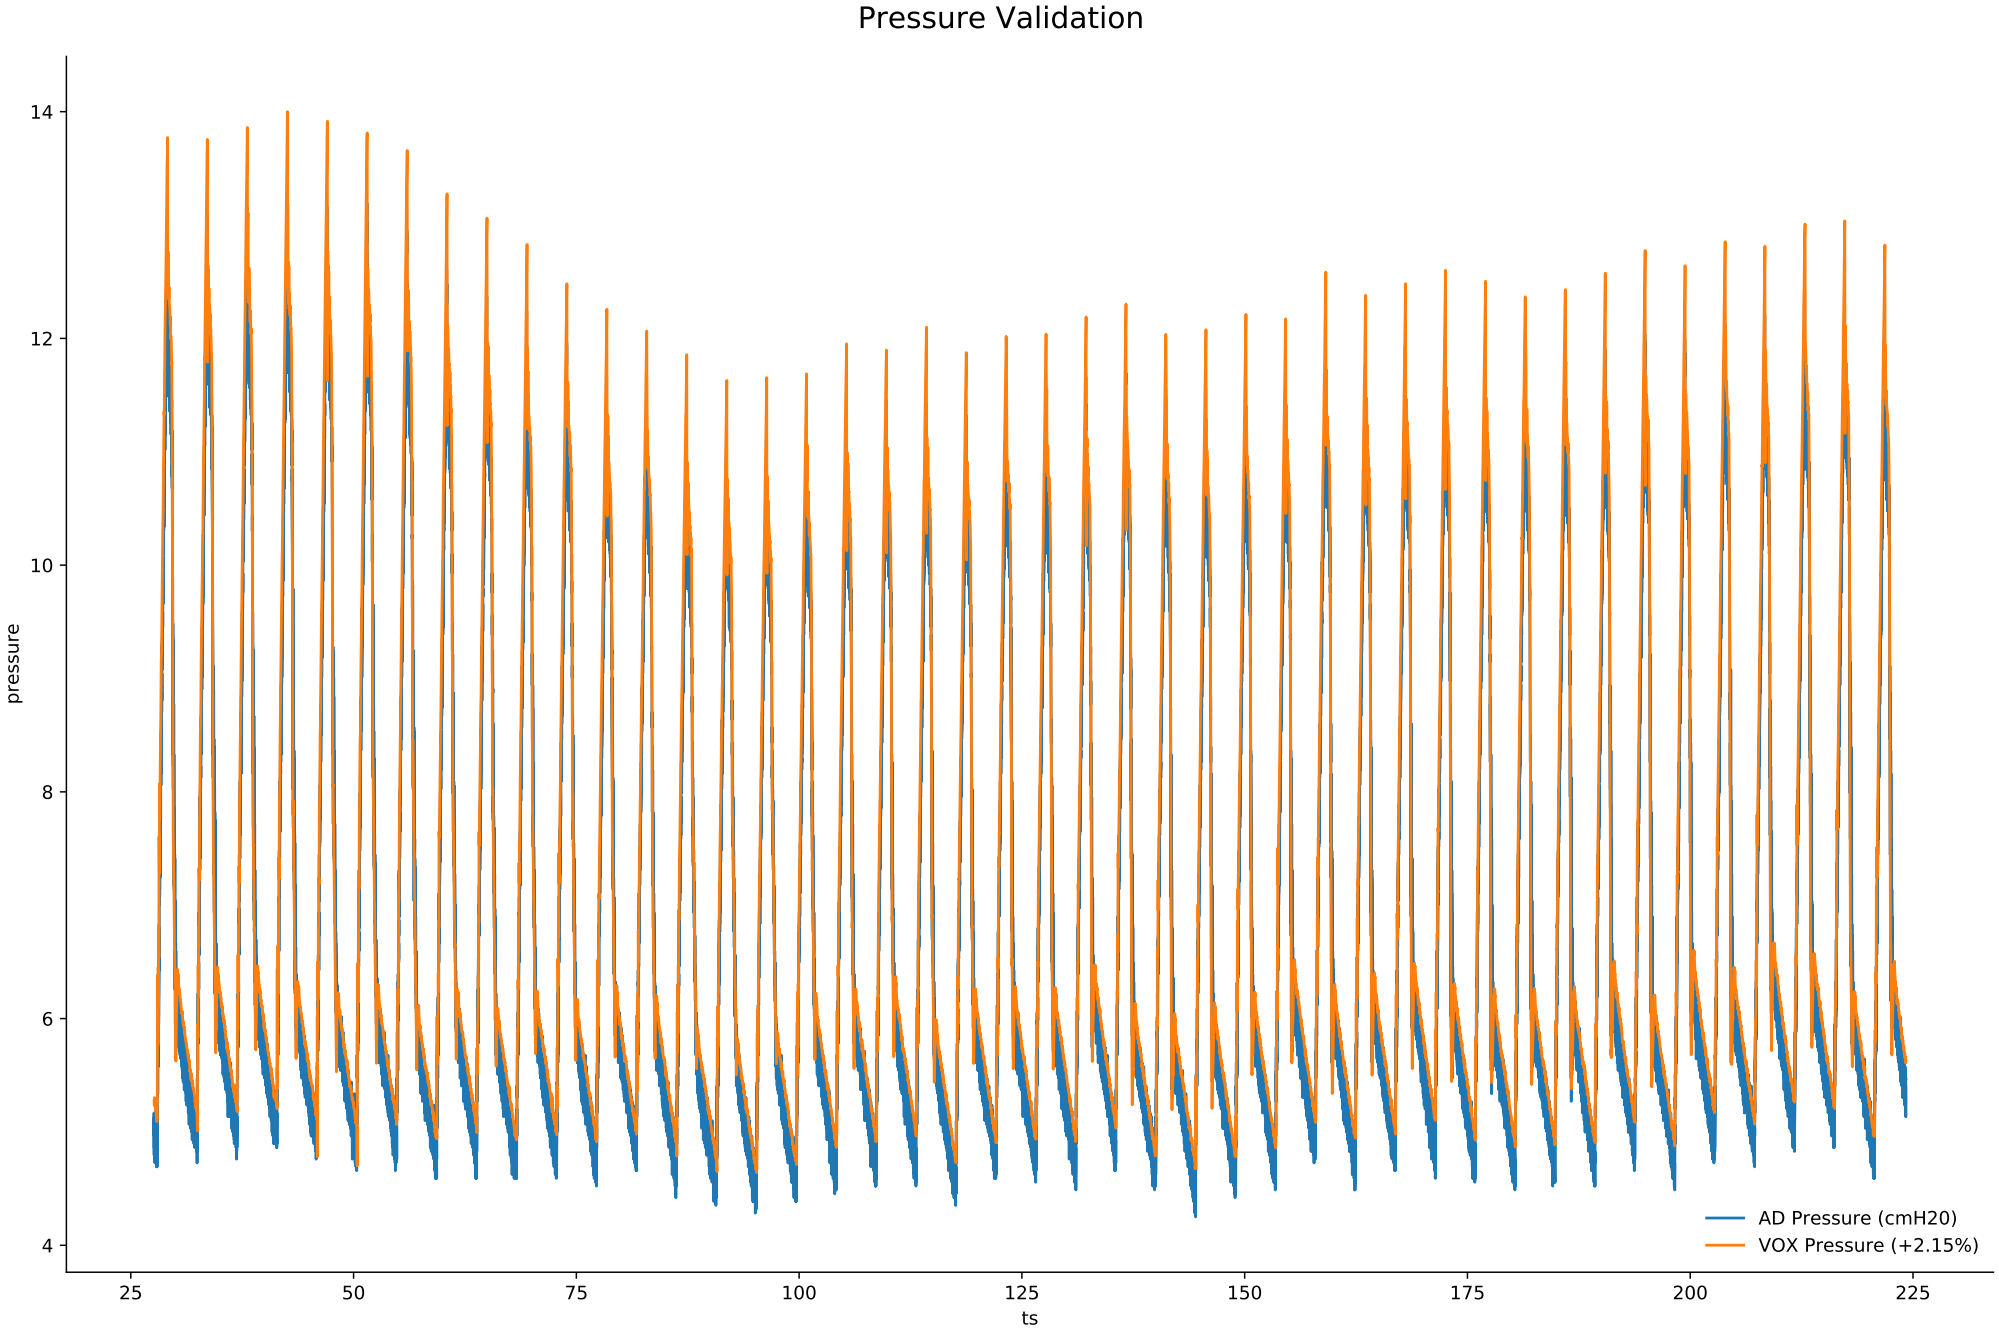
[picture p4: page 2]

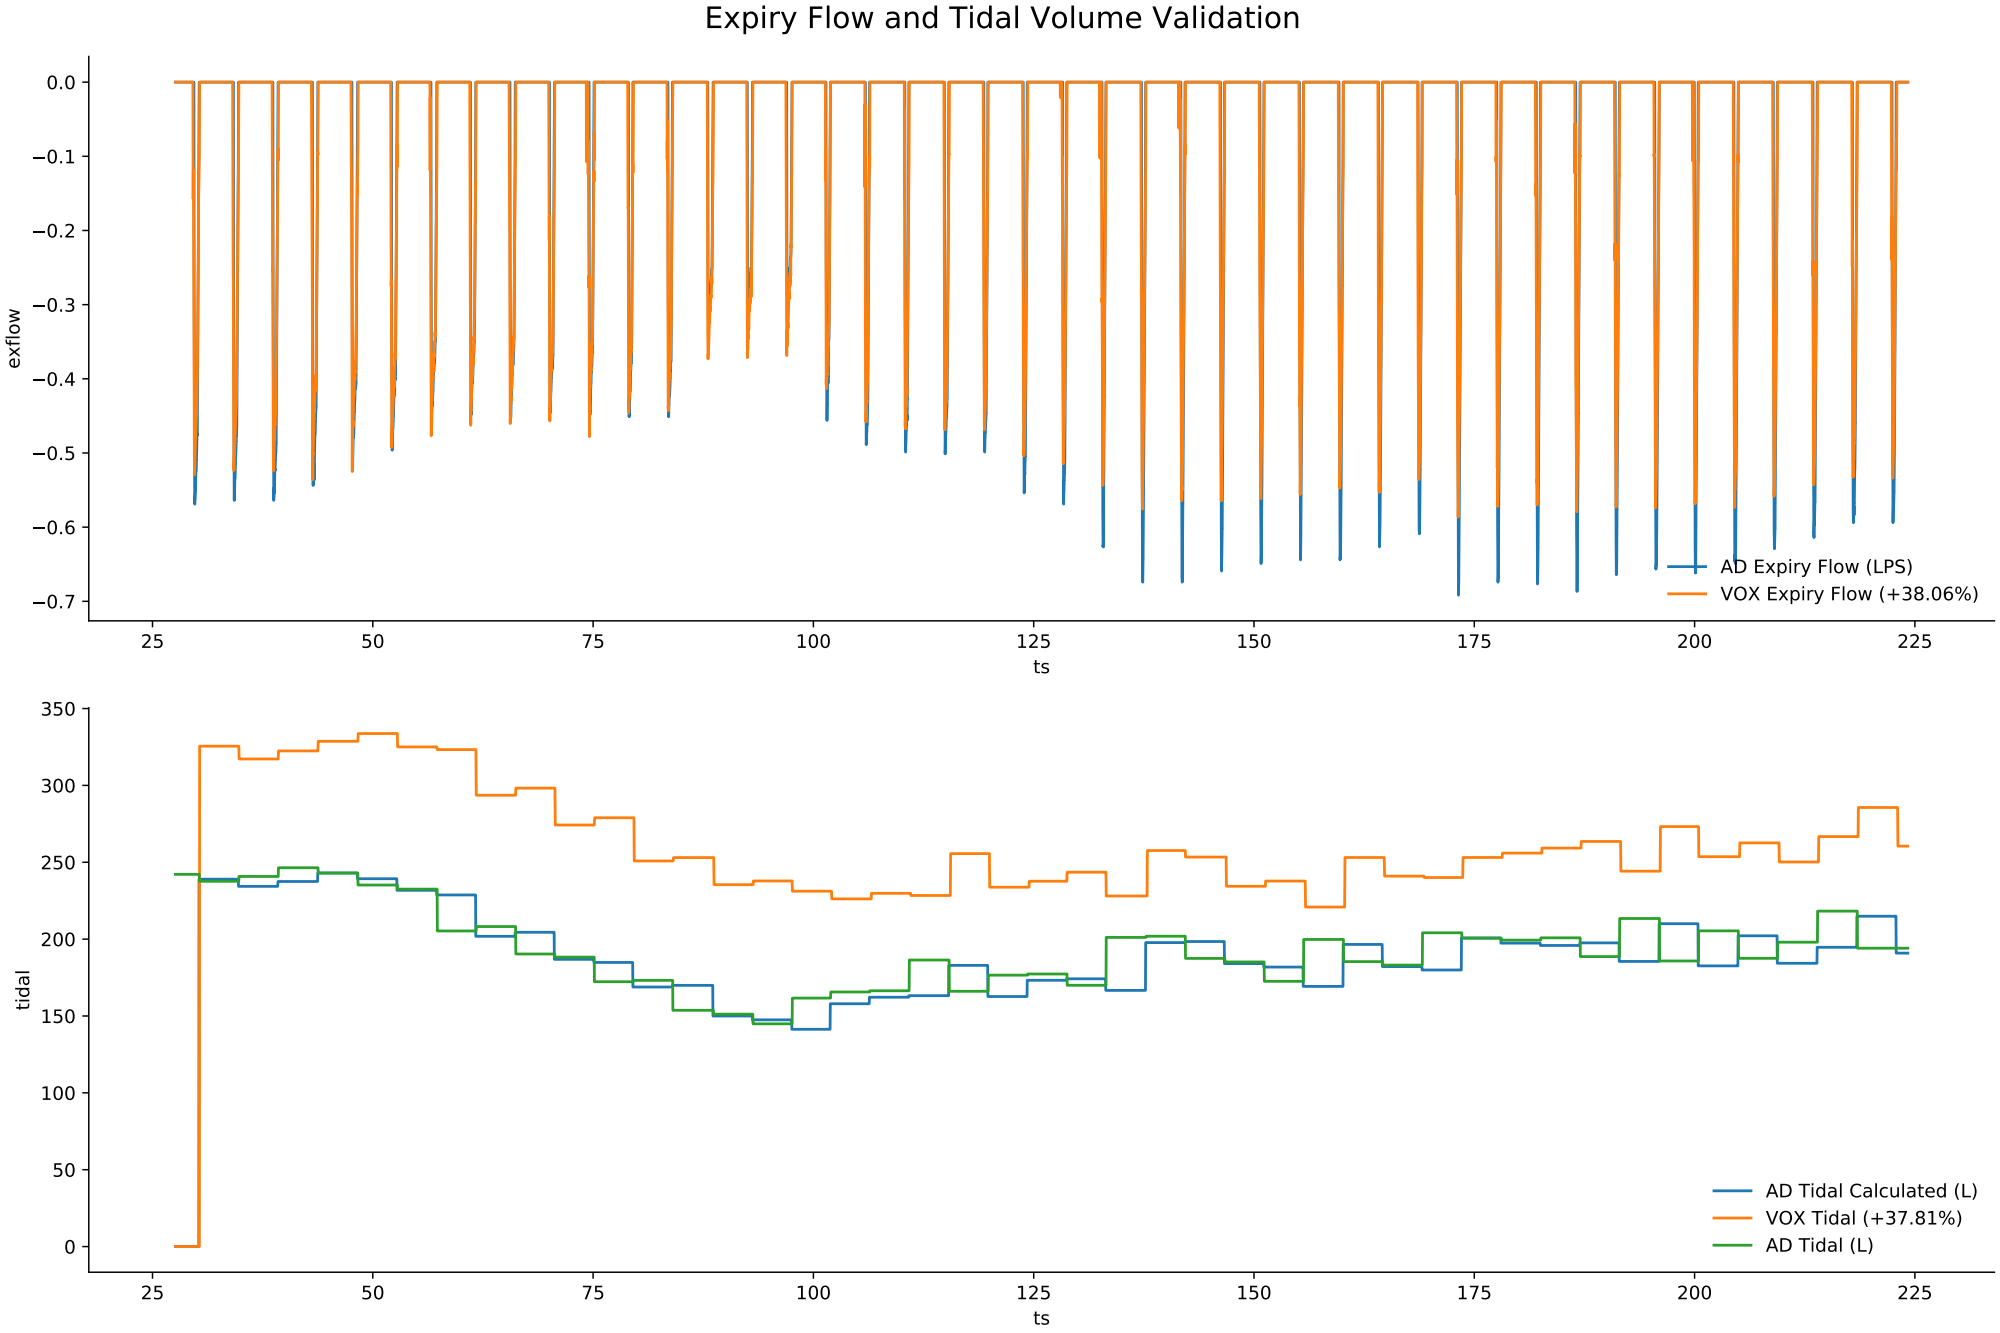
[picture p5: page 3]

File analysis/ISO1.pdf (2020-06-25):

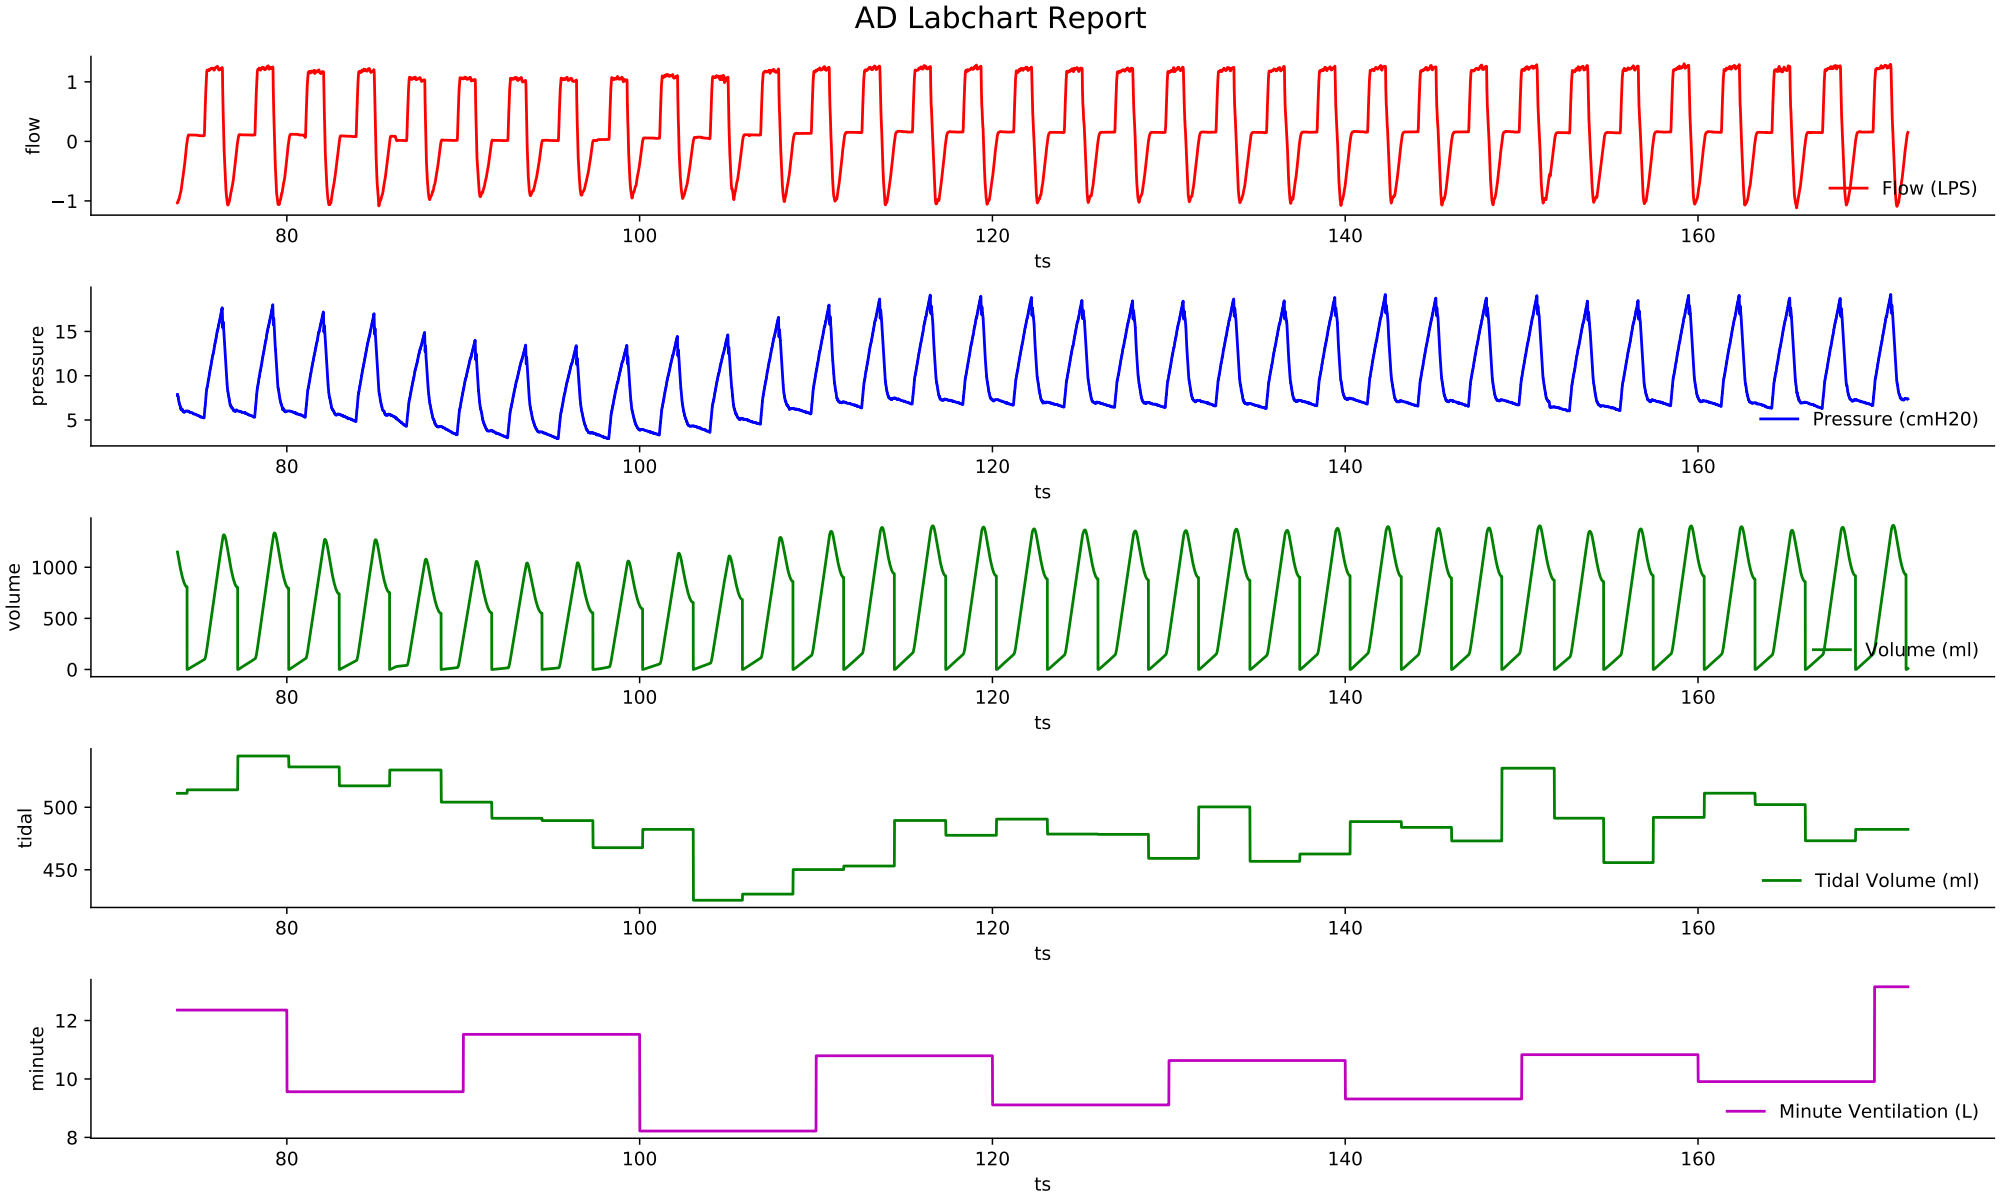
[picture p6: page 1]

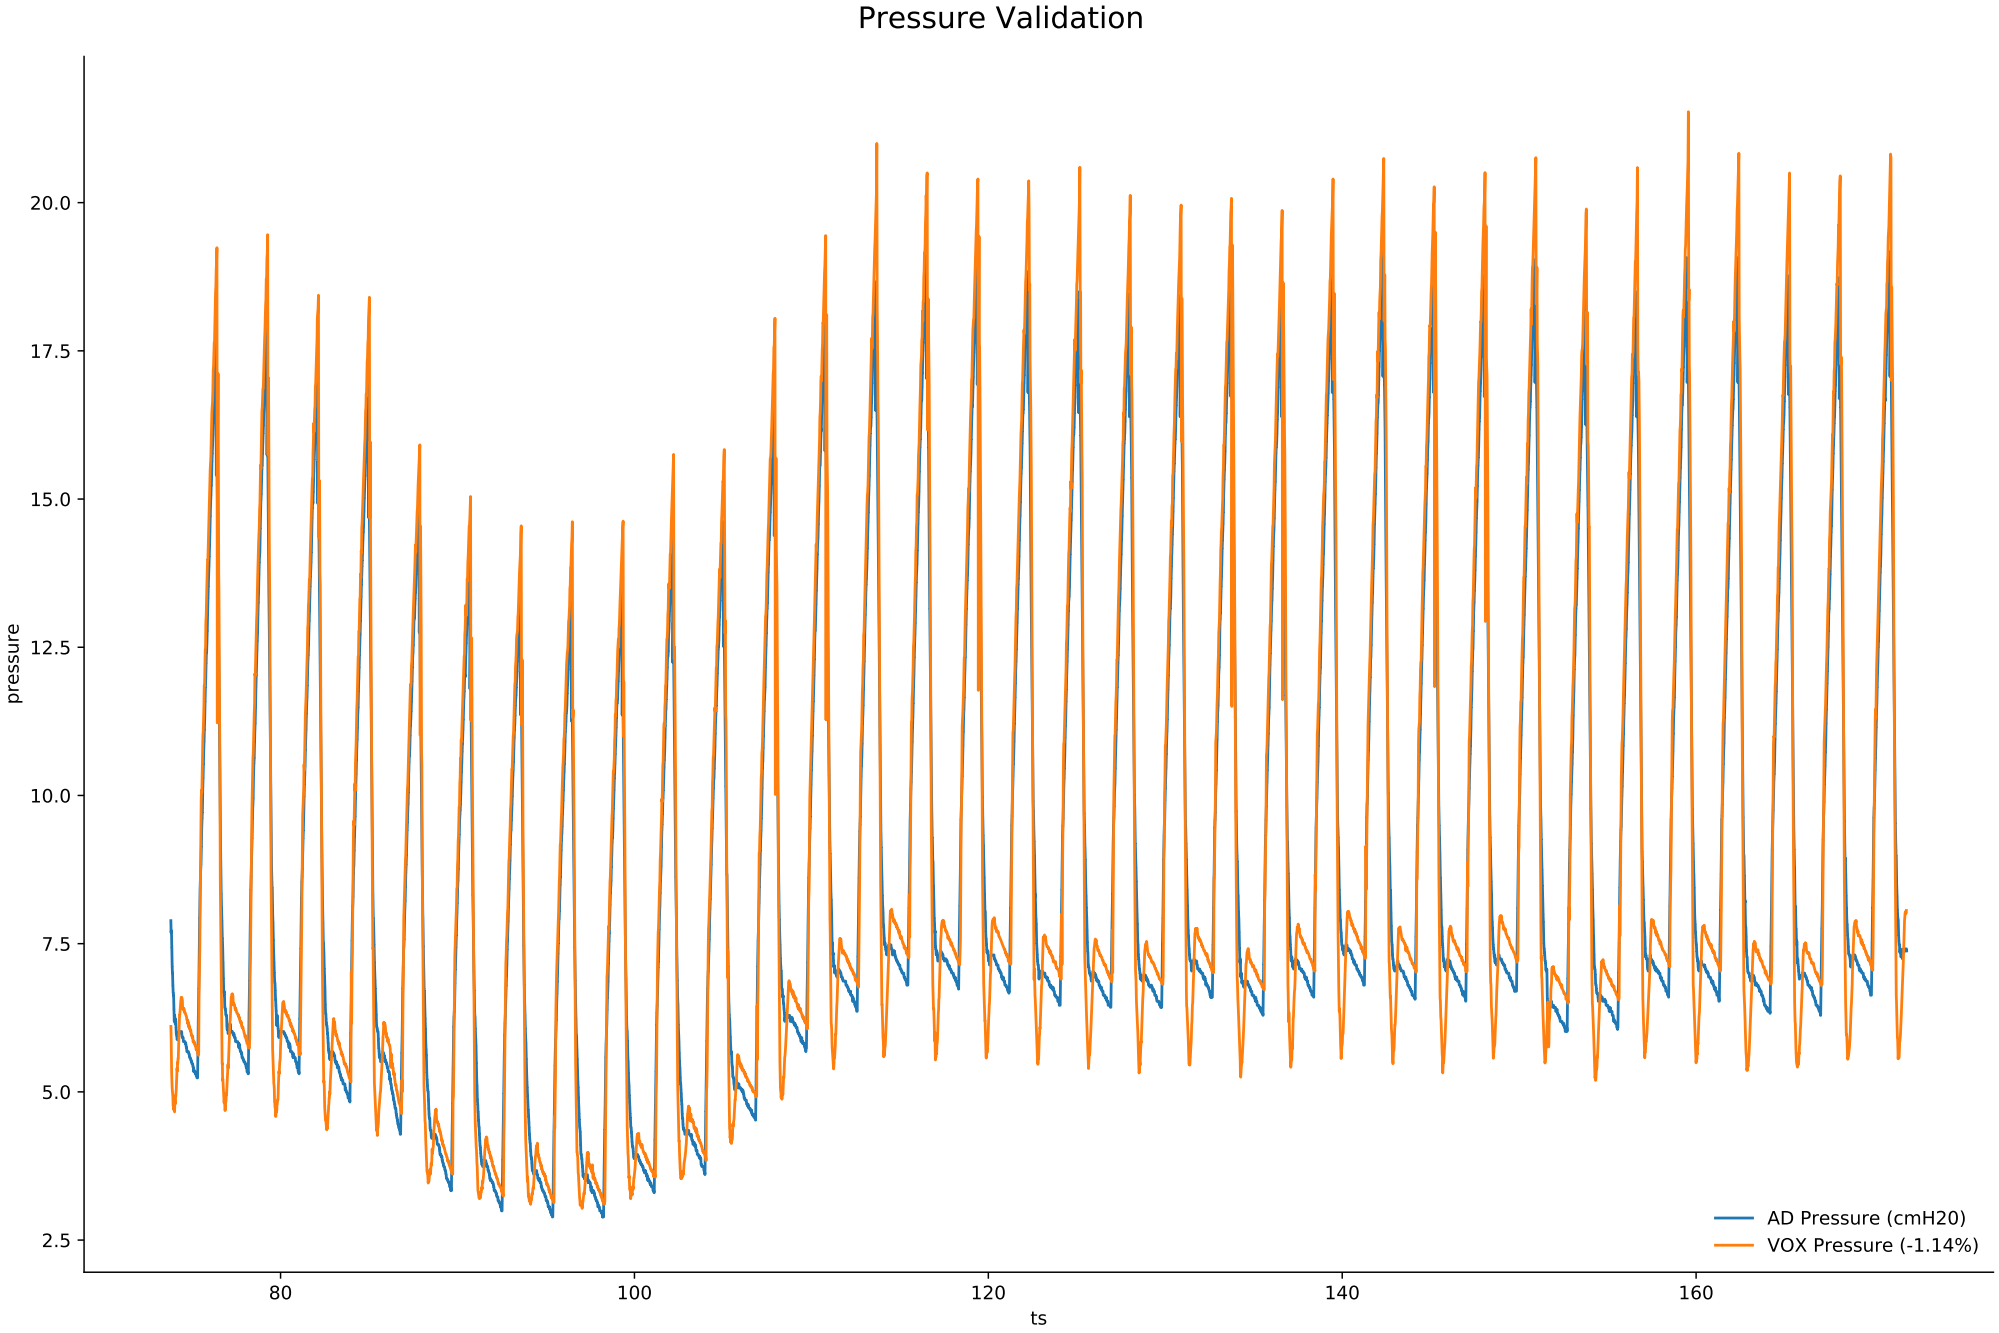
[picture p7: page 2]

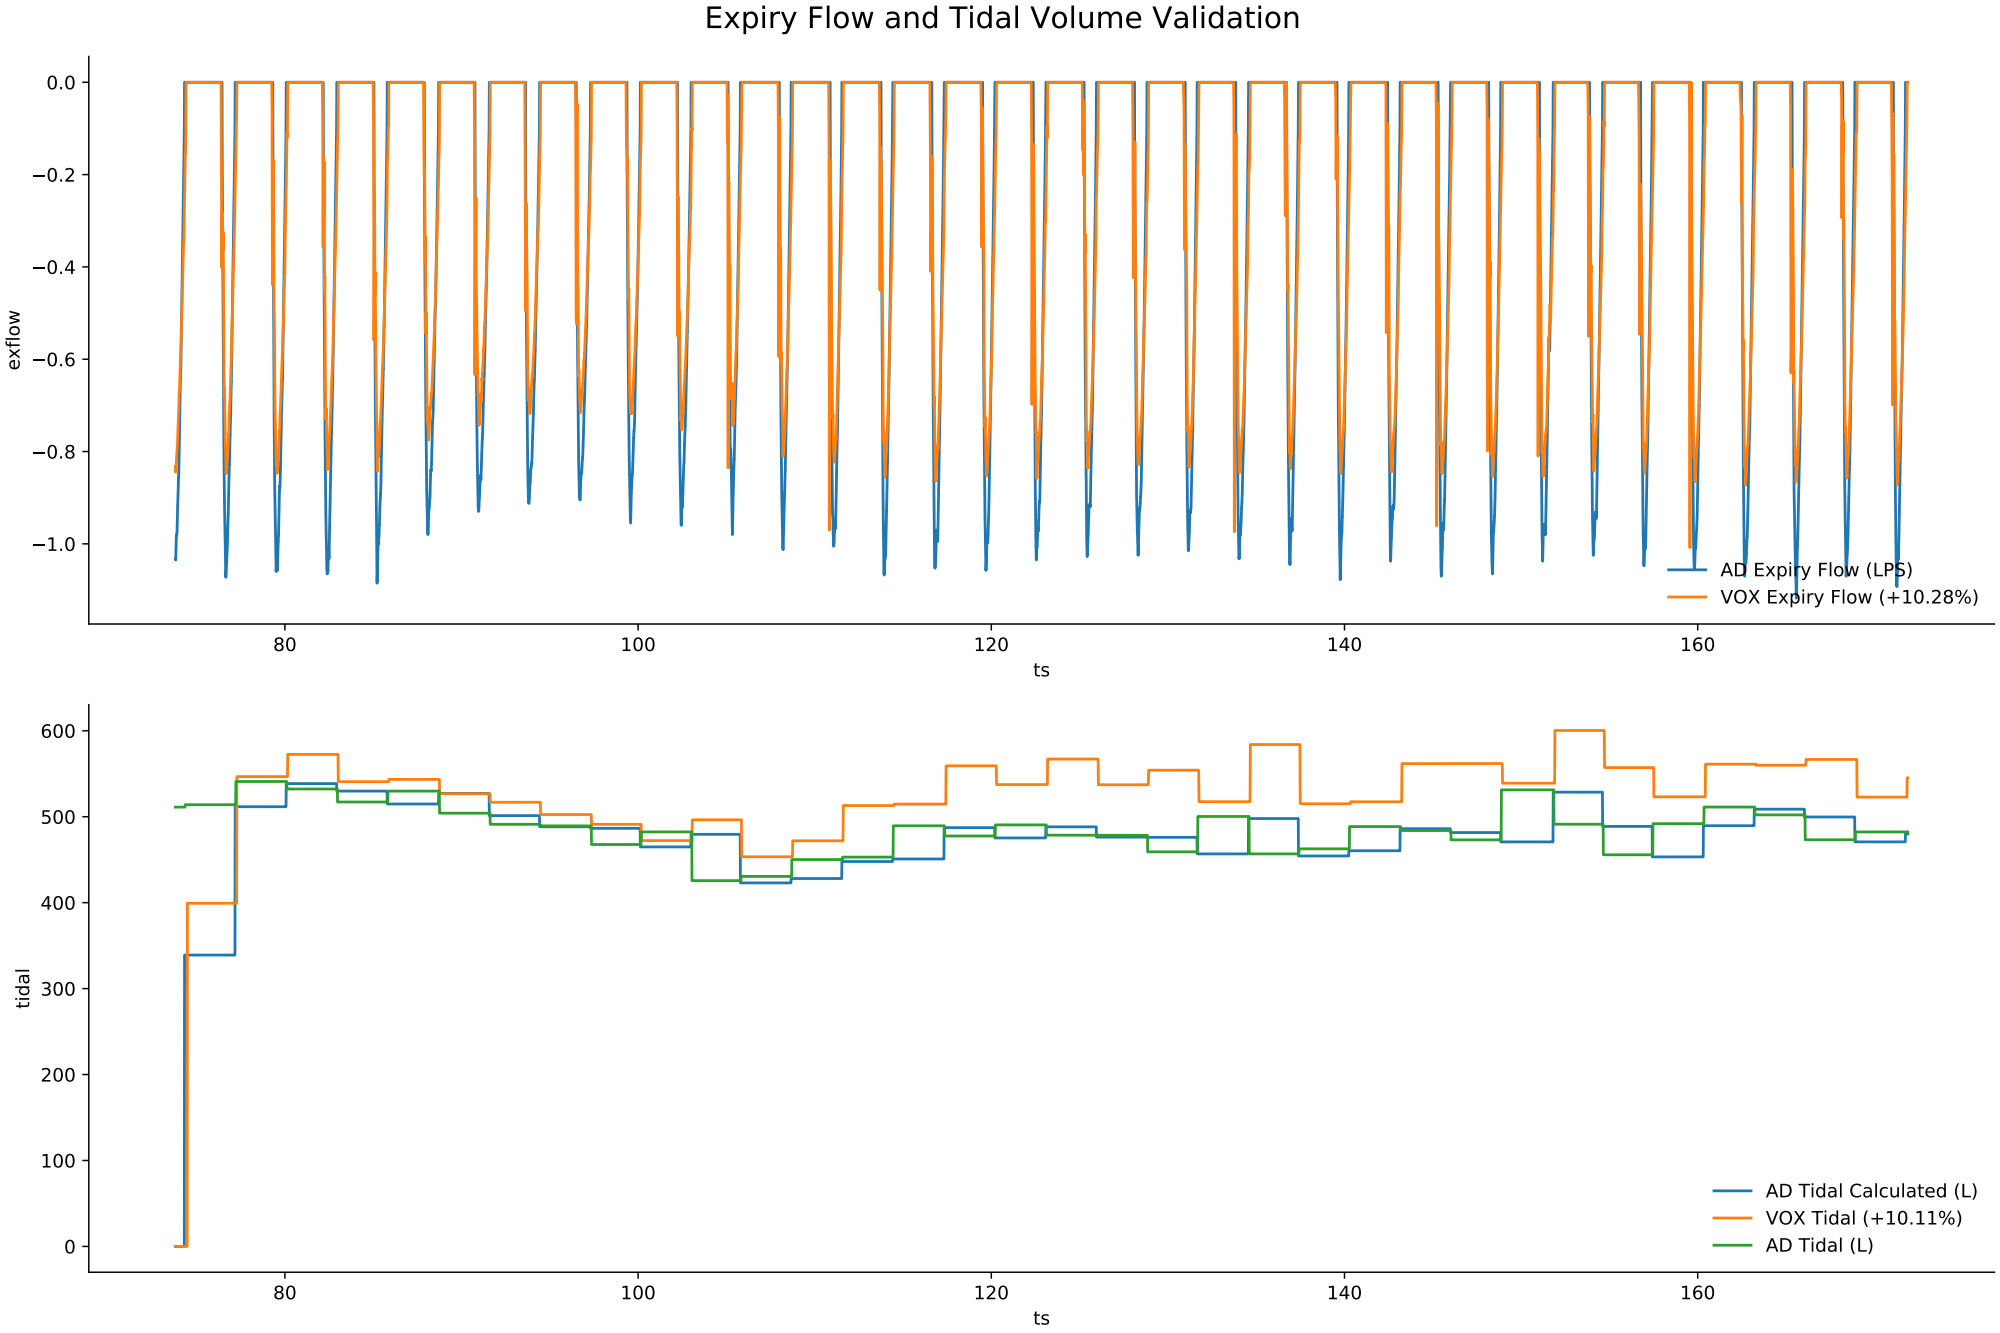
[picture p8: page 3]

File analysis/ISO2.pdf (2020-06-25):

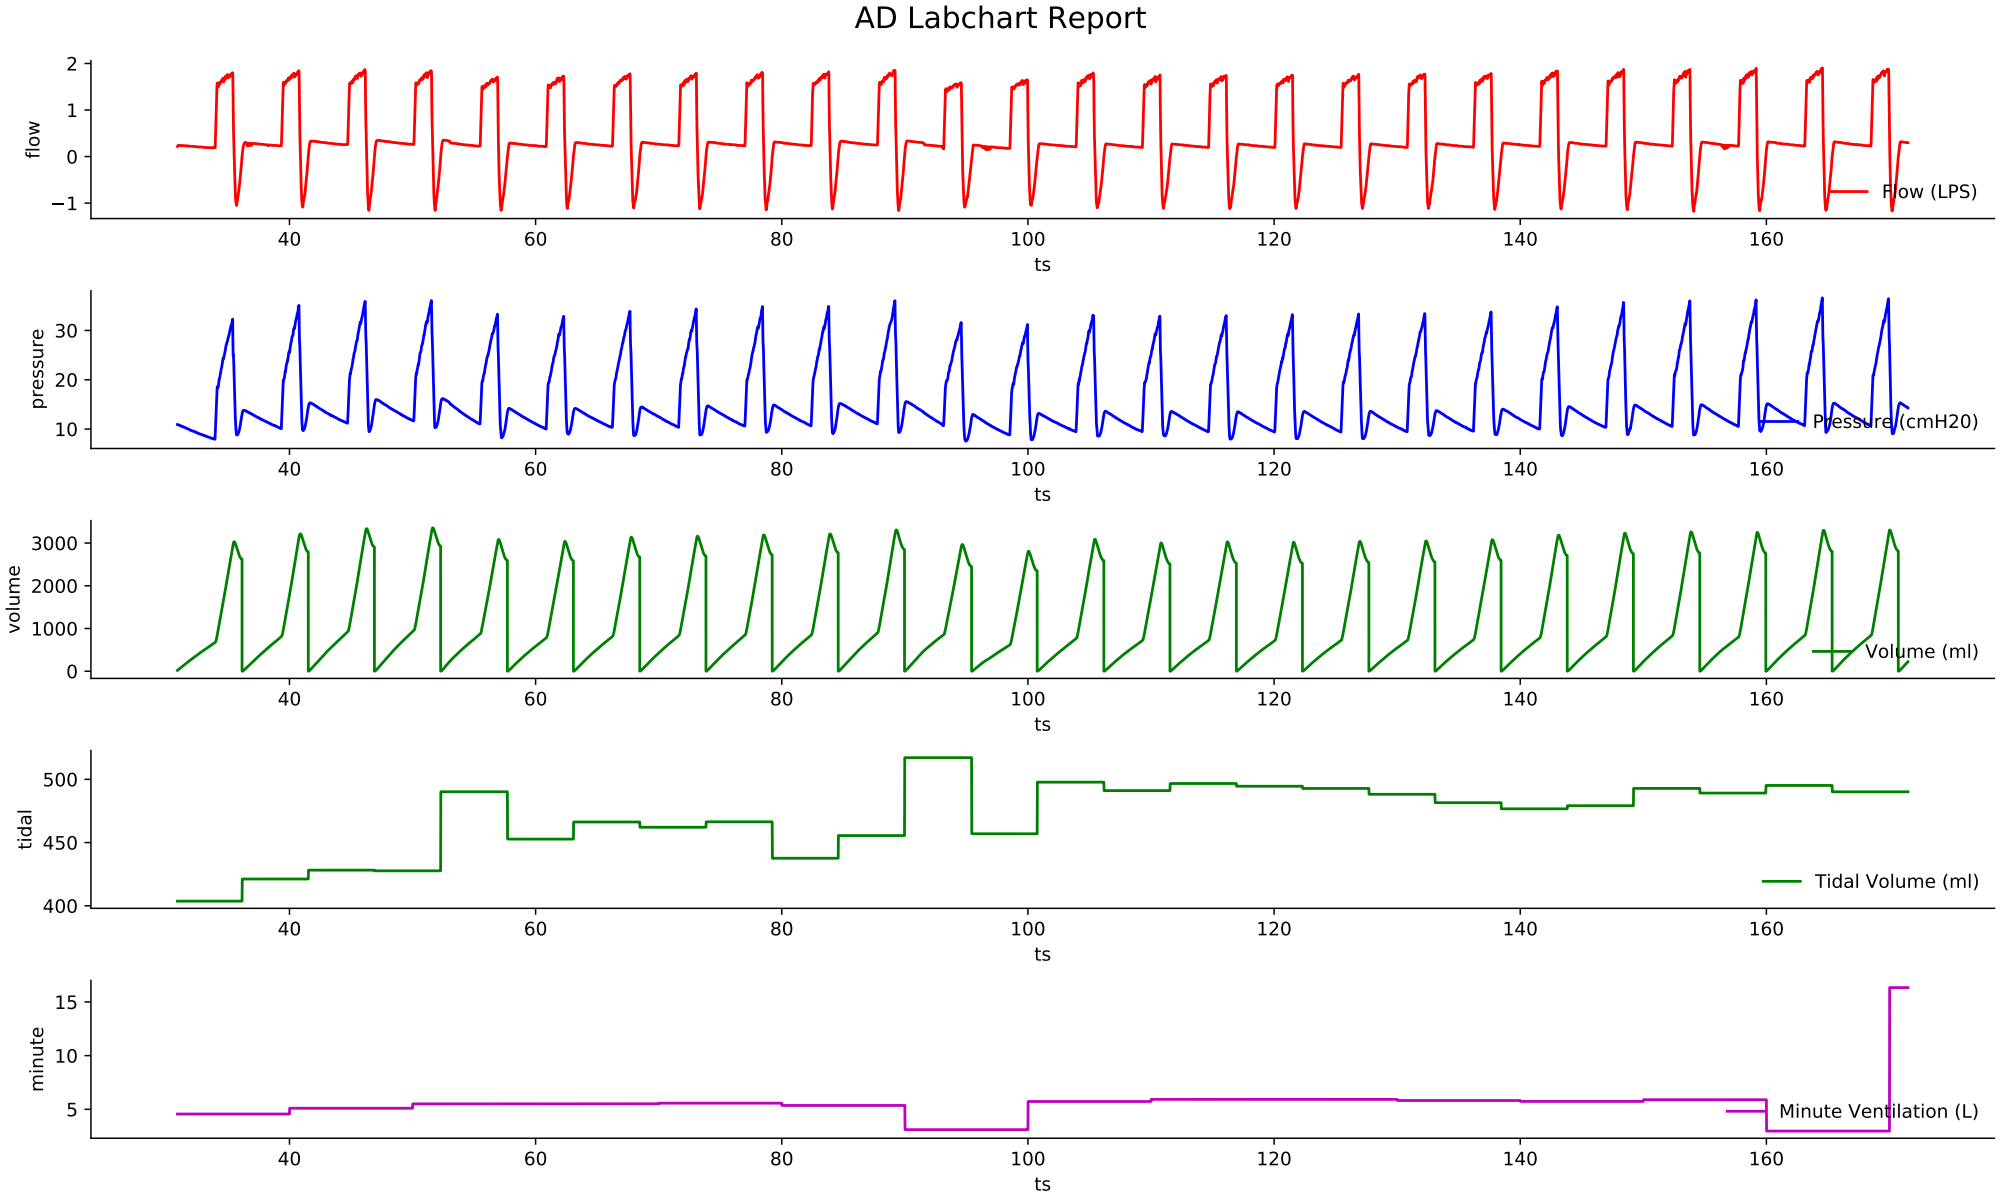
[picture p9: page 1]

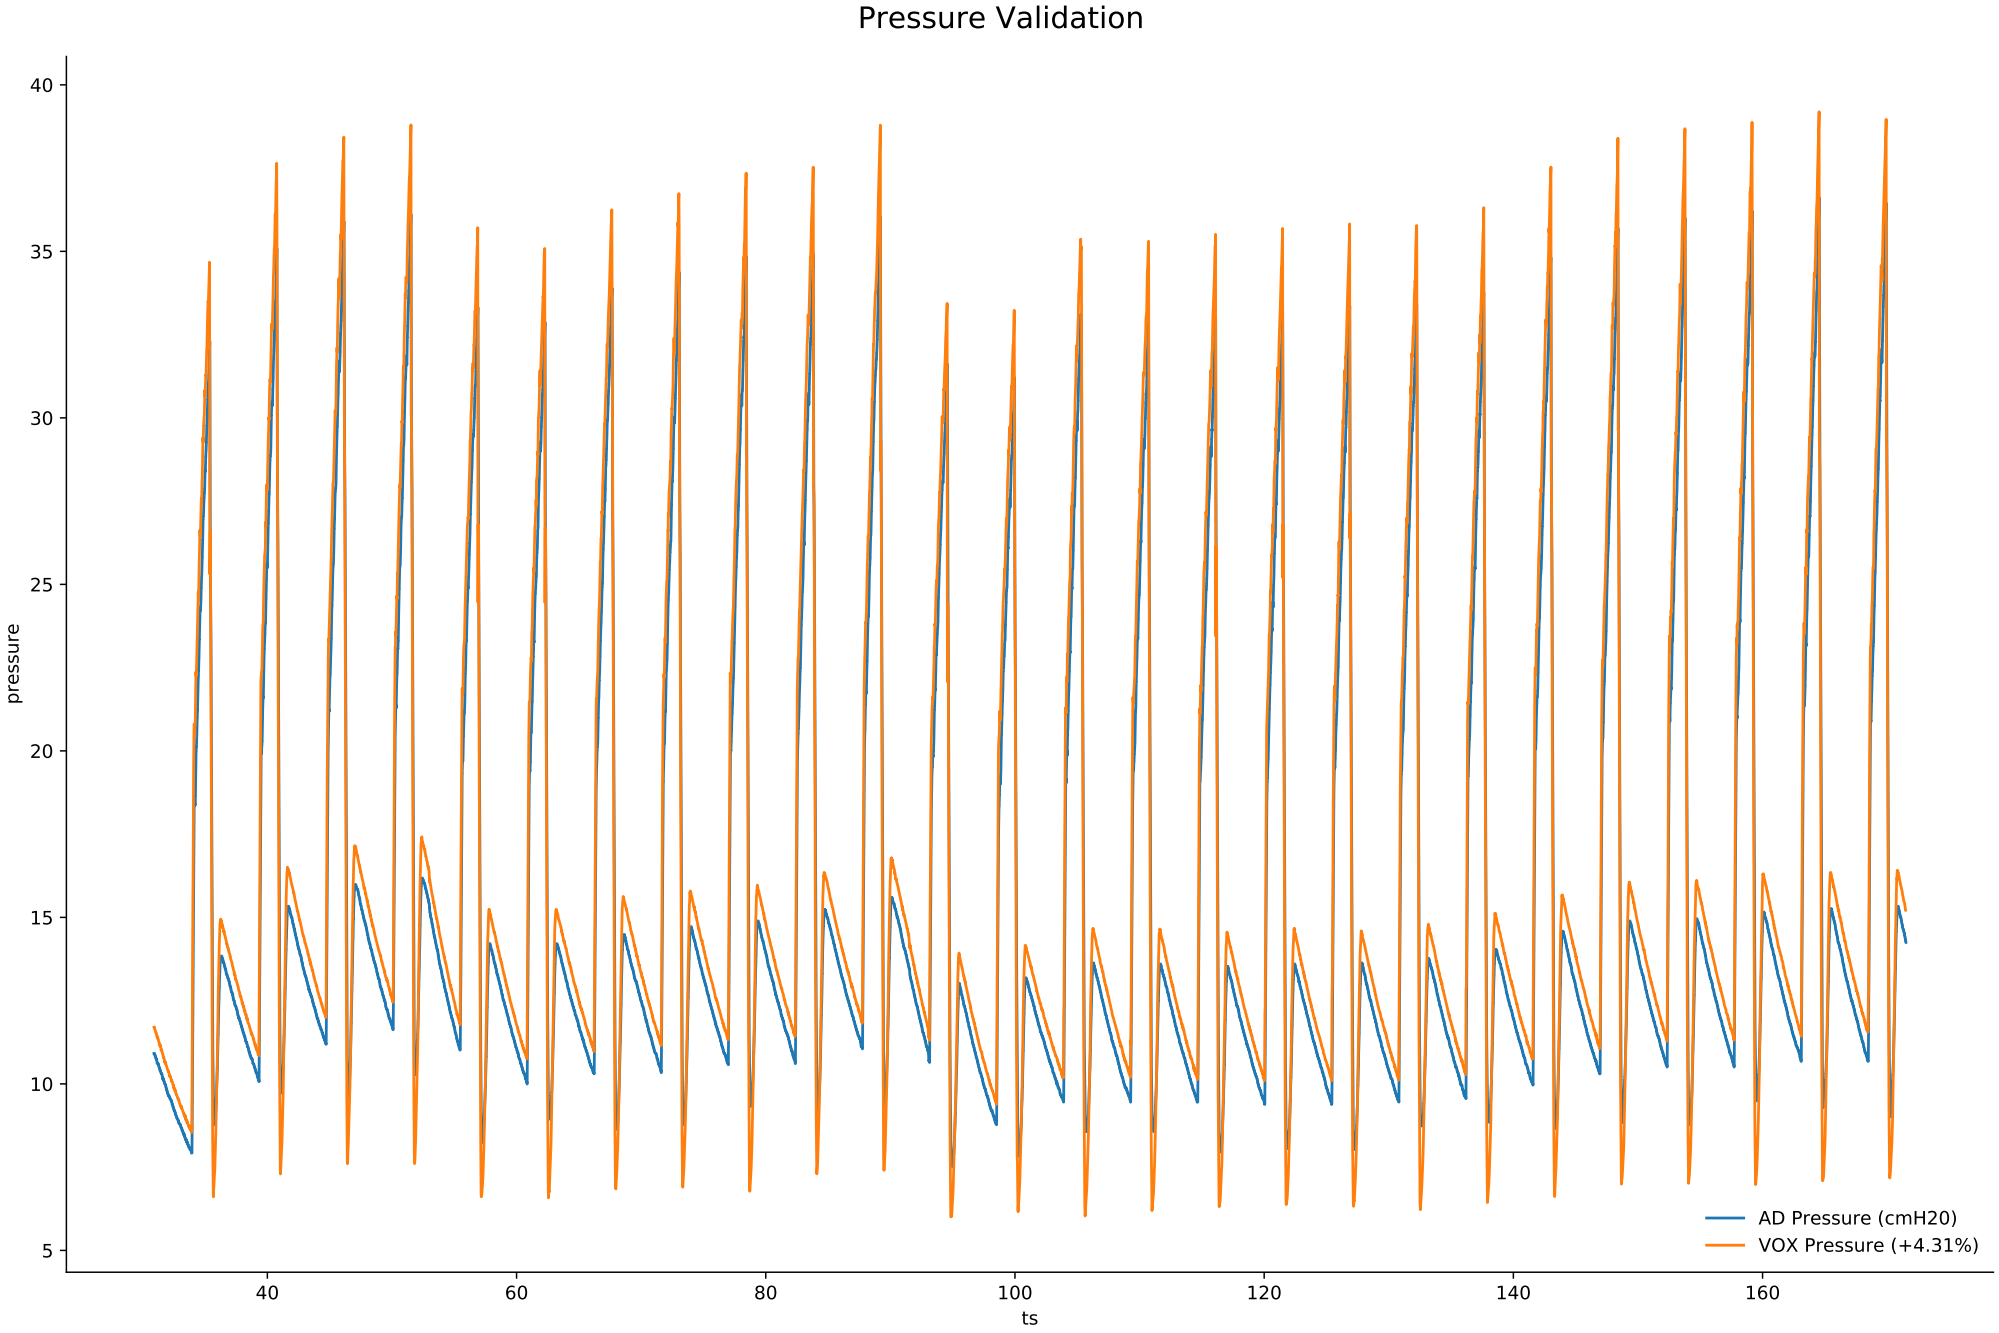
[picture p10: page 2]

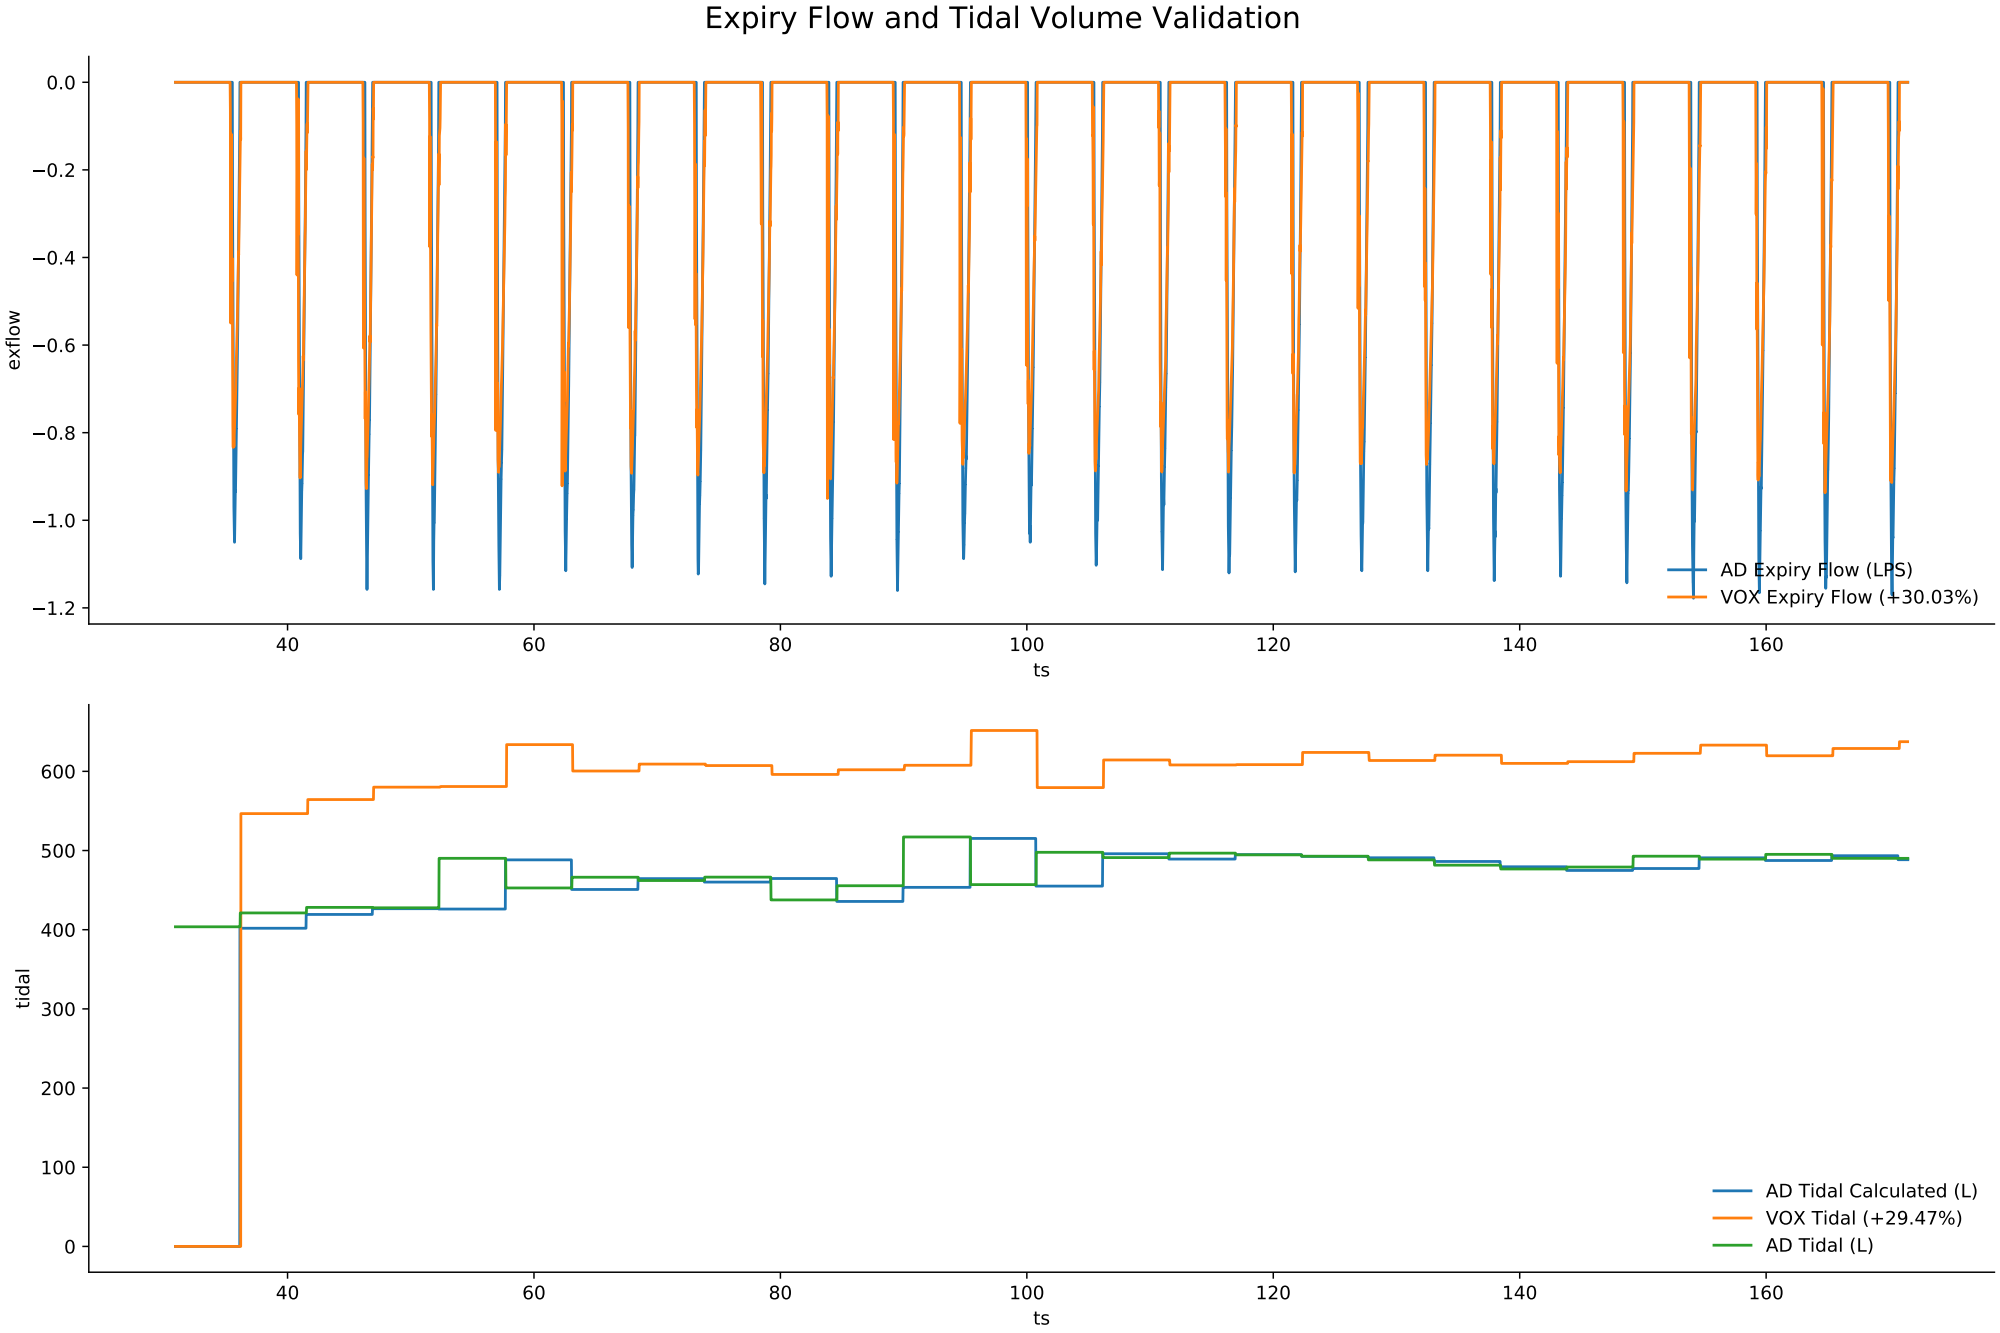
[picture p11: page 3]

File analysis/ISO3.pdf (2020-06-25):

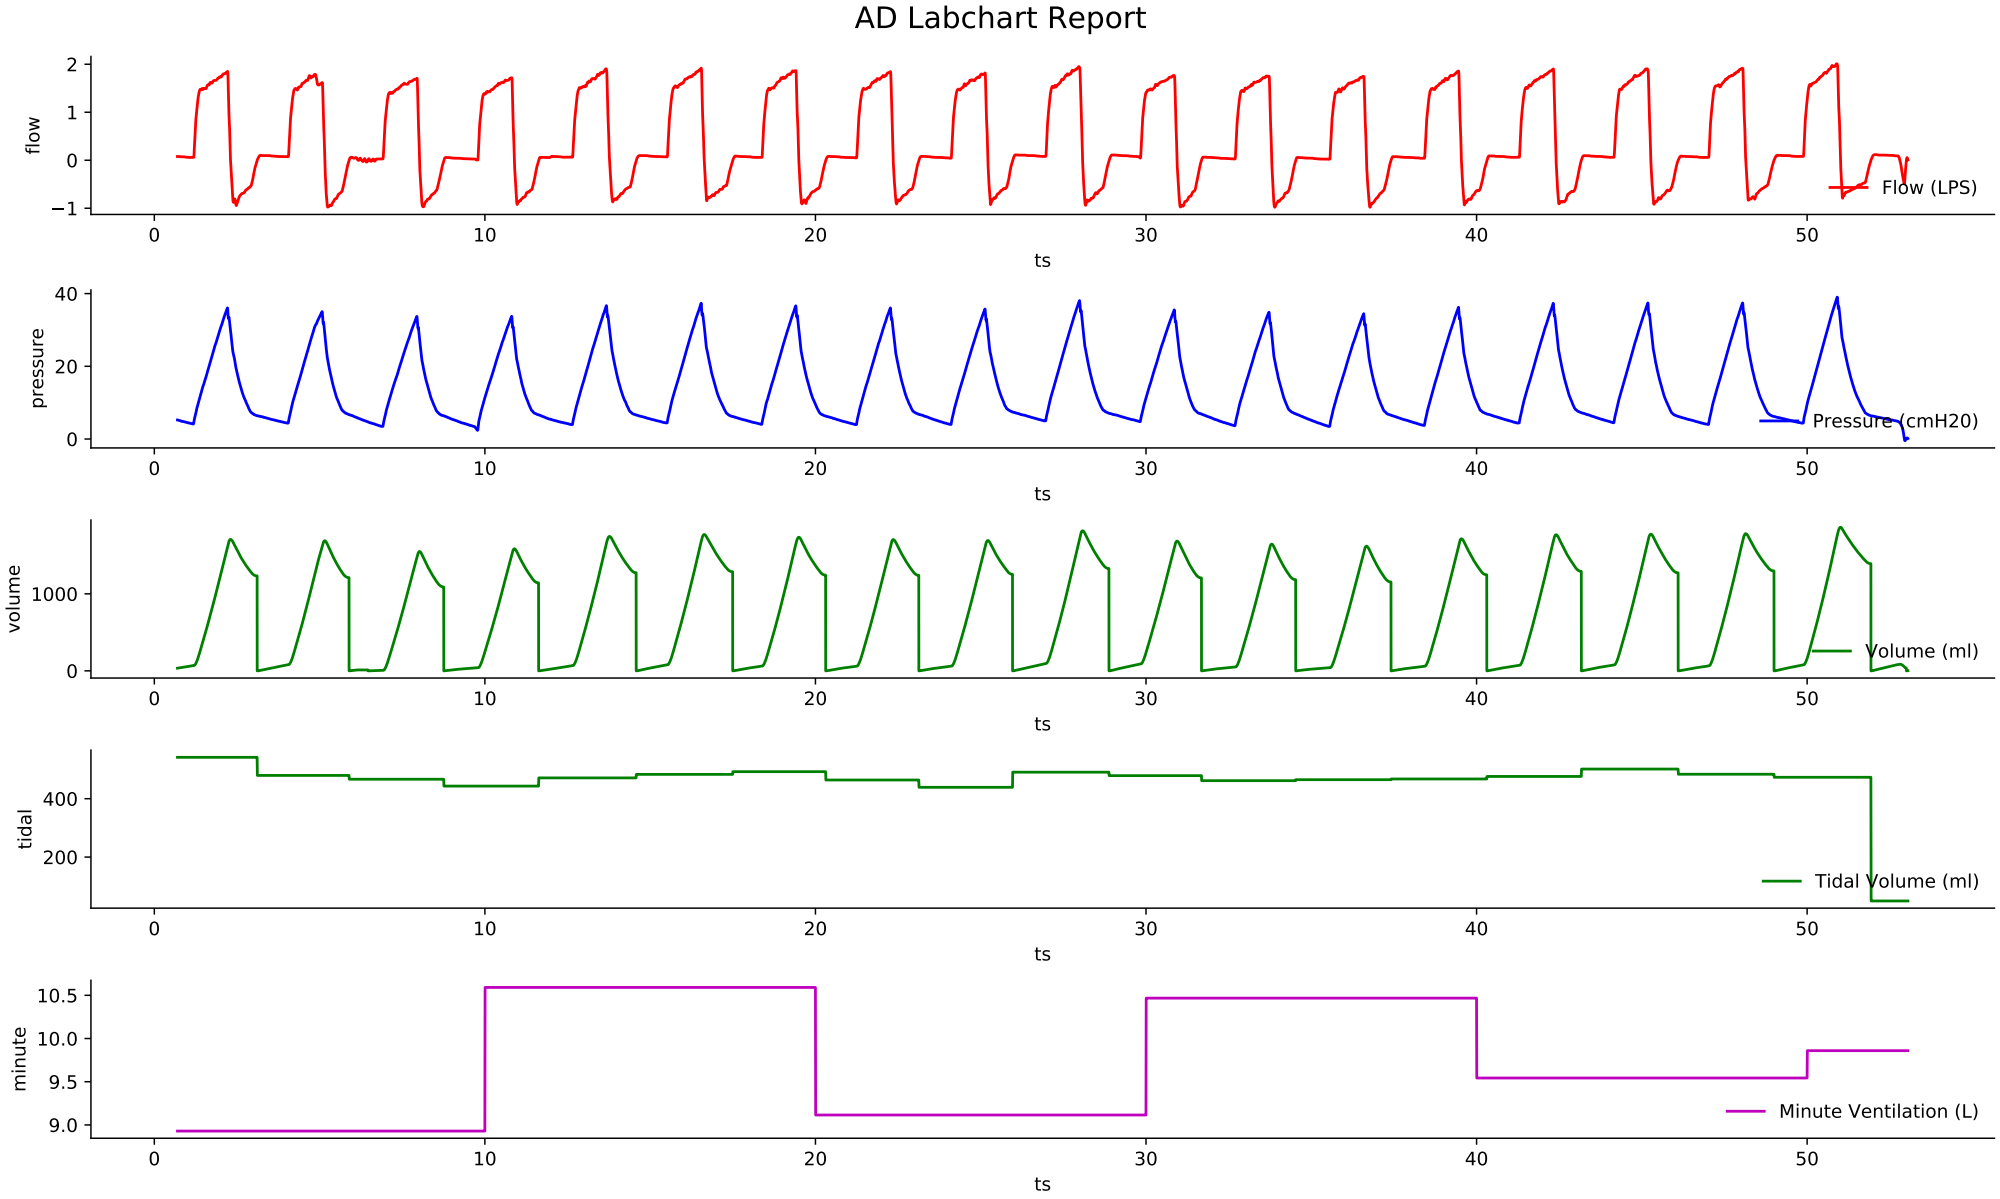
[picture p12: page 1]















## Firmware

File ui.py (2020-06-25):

#!/usr/bin/env python3                                                                                                                                       

from RPi import GPIO
from time import sleep
from evdev import UInput, ecodes as e
import logging
import time

CLK_PIN = 22
DT_PIN = 27
SW_PIN = 17
A_PIN = 9
B_PIN = 11
SPK_PIN = 10

GPIO.setmode(GPIO.BCM)
# rotary
GPIO.setup(CLK_PIN, GPIO.IN, pull_up_down=GPIO.PUD_DOWN)
GPIO.setup(DT_PIN, GPIO.IN, pull_up_down=GPIO.PUD_DOWN)
# buttons
GPIO.setup(SW_PIN, GPIO.IN, pull_up_down=GPIO.PUD_DOWN)
GPIO.setup(A_PIN, GPIO.IN, pull_up_down=GPIO.PUD_DOWN)
GPIO.setup(B_PIN, GPIO.IN, pull_up_down=GPIO.PUD_DOWN)
#speaker
GPIO.setup(SPK_PIN, GPIO.OUT)
#ui
ui = UInput()

# globals
g_counter = 0
g_clk = GPIO.input(CLK_PIN)

def _keystroke(key):
    logging.warning(key)
    ui.write(e.EV_KEY, key, 1)  # key down
    ui.write(e.EV_KEY, key, 0)  # key up
    ui.syn()

def knob_callback(c):
    logging.warning(c)
    _keystroke(e.KEY_K)

def a_callback(c):
    _keystroke(e.KEY_A)

def b_callback(c):
    _keystroke(e.KEY_S)

def rotary_callback(c):
    # adopted from Paul Versteeg
    # https://www.raspberrypi.org/forums/viewtopic.php?t=126753
    global g_counter
    global g_clk

    sleep(0.002) # extra 2 mSec de-bounce time

    clk = GPIO.input(CLK_PIN)
    dt = GPIO.input(DT_PIN)

    if (clk == 1) and (dt == 0) : # A then B ->
        g_counter += 1
        _keystroke(e.KEY_L)

        # at this point, B may still need to go high, wait for it
        while dt == 0:
            dt = GPIO.input(DT_PIN)
        # now wait for B to drop to end the click cycle
        while dt == 1:
            dt = GPIO.input(DT_PIN)

        return

    elif (clk == 1) and (dt == 1): # B then A <-
        g_counter -= 1
        _keystroke(e.KEY_J)
        # A is already high, wait for A to drop to end the click cycle
        while clk == 1:
            clk = GPIO.input(CLK_PIN)
        return

    else: # discard all other combinations
        return

def alarm(seconds):
    GPIO.output(SPK_PIN, 1)
    time.sleep(seconds)
    GPIO.output(SPK_PIN, 0)

def ui_loop():
    GPIO.add_event_detect(SW_PIN, GPIO.FALLING, callback=knob_callback, bouncetime=1200)
    GPIO.add_event_detect(A_PIN, GPIO.FALLING, callback=a_callback, bouncetime=1200)
    GPIO.add_event_detect(B_PIN, GPIO.FALLING, callback=b_callback, bouncetime=1200)
    GPIO.add_event_detect(CLK_PIN, GPIO.RISING, callback=rotary_callback, bouncetime=2)
    logging.warning("UI running press anything to exit")
    
if __name__ == '__main__':
    ui_loop()
    while True:
        user = input()
        if (user == ""):
            break
        try:
            seconds = int(user)
            alarm(seconds)
        except Exception as e:
            print(e)

    GPIO.cleanup()
    ui.close()
    

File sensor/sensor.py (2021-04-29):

# Sensor Manager
import time
from datetime import datetime
from multiprocessing import Process, Queue, Array, Value
import logging

import board
import busio

import rpi2c
import constants

from sensor import oxygen
    
from sensor.sensor_lps import PressureSensorLPS

i2c_in = rpi2c.rpi_i2c(1)
i2c_ex = rpi2c.rpi_i2c(3)


"""
venturi coefficient - https://www.efunda.com/formulae/fluids/venturi_flowmeter.cfm

60000 * 0.975 * (pi/4) * D2^2 * ( (2 * dP) / (1.204 * (1 - (D2/D1)^4))^0.5

where:
  60000 is conversion from m^3/s to L/min
  0.975 is the discharge coefficient 
         usually lies between 0.90 and 0.98 for smoothly tapering venturis
  1.204 air density at sea level

assumptions:
  
and:
  D2 = 19.05mm
  D1 = 6.35mm
"""

VCO = 2.40256
MAXPA = 4000

def check_spontaneous(pressure, breathing, assist):
    if assist.value > 0 and pressure < -(assist.value) and breathing.value == 0:
        logging.warn("spontaneous breath initiated")
        breathing.value = 1

def check_peep(pressure, breathing, peeping, peepx):
    if breathing.value == constants.EXPIRING and peeping.value != constants.CLOSED and pressure < peepx.value:
        logging.warning("crosssing peepx on expire %d < %d" % (pressure, peepx.value))
        peeping.value = constants.CLOSED

def pressure_prime(pressure_in_1, pressure_in_2, pressure_ex_1, pressure_ex_2):
    for i in range(0,100):
        time.sleep(0.005)
        pressure_in_1.read()
        pressure_in_2.read()
        pressure_ex_1.read()
        pressure_ex_2.read()

def pressure_zero(pressure_in_1, pressure_in_2, pressure_ex_1, pressure_ex_2):
    pressure_prime(pressure_in_1, pressure_in_2, pressure_ex_1, pressure_ex_2)
    pressure_in_1.zero_pressure()
    pressure_in_2.zero_pressure()
    pressure_ex_1.zero_pressure()
    pressure_ex_2.zero_pressure()
    pressure_prime(pressure_in_1, pressure_in_2, pressure_ex_1, pressure_ex_2)

def sensor_loop(times, flow, volume, tidal, o2_percent,
                pmin, pmax, expire, breathing, peeping,
                in_pressure_1, in_pressure_2, in_flow,
                ex_pressure_1, ex_pressure_2, ex_flow,
                idx, count, assist, peepx):

    # inspiration
    pressure_in_1 = PressureSensorLPS(i2c_in, address=0x5d)
    pressure_in_2 = PressureSensorLPS(i2c_in, address=0x5c)

    # expiration
    pressure_ex_1 = PressureSensorLPS(i2c_ex, address=0x5d)
    pressure_ex_2 = PressureSensorLPS(i2c_ex, address=0x5c)

    # oxygen
    try:
        o2_sensor = oxygen.OxygenADS(i2c_in)
    except:
        logging.error("o2 not found - using mock")
        o2_sensor = oxygen.MockOxygen(i2c_in)
    
    # calibrate sensors
    pressure_zero(pressure_in_1, pressure_in_2, pressure_ex_1, pressure_ex_2)
    o2_sensor.calibrate()
    
    # open diagnostics outfile
    fname = datetime.now().strftime("%Y-%m-%d-%H-%M-%S.out")
    f = open(fname, "wb", 0)

    # state management
    state_breathing = 0        # valve open when breathing = 1
    state_volume_sum = 0       # accumulator to track volume (inhalation - exhalation)
    state_sample_sum = 0       # accumulator to track samples
    state_last_samples = 75    # calculated number of samples in last breath 
    state_tidal_sum = 0        # accumulator to track tidal volume (exhalation volume)
    state_last_tidal = 0       # calculated tidal volume of last breath
    state_pmin_min = MAXPA     # minimum pressure per breath cycle
    state_last_pmin = 0        # calculated min pressure in last breath cycle
    state_pmax_max = 0         # maximum pressure per breath cycle
    state_last_pmax = 0        # calculate max pressure in last breath cycle
    state_start_expire = 0     # start of last exspire
    state_last_expire = 0      # calculated expiry time per breath cycle
    
    while True:
        pressure_in_1.read()
        pressure_in_2.read()
        pressure_ex_1.read()
        pressure_ex_2.read()

        i = idx.value + 1
        if i >= count.value:
            i = 0

        # update timestamp
        ts = time.time()
        times[i] = ts
        
        # inspiration
        p1 = pressure_in_1.data.pressure
        p2 = pressure_in_2.data.pressure
        in_pressure_1[i] = p1 / 98.0665 # convert from Pa to cmH2O
        in_pressure_2[i] = p2 / 98.0665 # convert from Pa to cmH2O
        in_flow[i] = VCO * (abs(p2-p1)**0.5)
        
        # expiration
        p1 = pressure_ex_1.data.pressure
        p2 = pressure_ex_2.data.pressure
        ex_pressure_1[i] = p1 / 98.0665 # convert from Pa to cmH2O
        ex_pressure_2[i] = p2 / 98.0665 # convert from Pa to cmH2O
        ex_flow[i] = VCO * (abs(p2-p1)**0.5)
        
        # oxygen
        o2_percent[i] = o2_sensor.read()
        
        if (breathing.value == constants.INSPIRING):
            # transition from expire to inspire reset volume state calculations
            if state_breathing == 0:
                state_breathing = 1
                state_volume_sum = 0
                state_last_tidal = state_tidal_sum
                state_tidal_sum = 0
                state_last_samples = state_sample_sum
                state_sample_sum = 0
                state_last_pmin = state_pmin_min
                state_pmin_min = MAXPA
                state_last_pmax = state_pmax_max
                state_pmax_max = 0
                if state_start_expire > 0:
                    state_last_expire = ts - state_start_expire
                    state_start_expire = 0
            # update inspiration metrics
            state_volume_sum += in_flow[i]
            flow[i] = in_flow[i]

        elif breathing.value == constants.EXPIRING:
            # transition from inspire to expire capture time
            if state_breathing == 1:
                state_breathing = 0
                state_start_expire = ts
            # update expiration metrics            
            state_tidal_sum += ex_flow[i]
            state_volume_sum -= ex_flow[i]
            flow[i] = -ex_flow[i]
            
        else:
            # valves closed clear flow and volume
            flow[i] = 0
            state_volume_sum = 0

        # track min and max pressures
        peep_pressure = ex_pressure_2[i]
        check_peep(peep_pressure, breathing, peeping, peepx)
        state_pmax_max = max(state_pmax_max, peep_pressure)
        state_pmin_min = min(state_pmin_min, peep_pressure)

        state_sample_sum += 1
        volume[i] = state_volume_sum / state_last_samples * 60 # volume changes throughout breathing cycle
        tidal[i] = state_last_tidal / state_last_samples * 60  # tidal volume counted at end of breathing cycle        
        pmin[i] = state_last_pmin                              # minimum pressure at end of last breathing cycle
        pmax[i] = state_last_pmax                              # maximum pressure at end of last breathing cycle
        expire[i] = state_last_expire                          # expiration time of last breath

        check_spontaneous(in_pressure_2[i], breathing, assist)

        f.write(bytearray(b"%f %f %f %f %f %f %f %f %f %f\n" % (
            times[i],
            flow[i],
            volume[i],
            tidal[i],
            in_pressure_1[i],
            in_pressure_2[i],
            in_flow[i],
            ex_pressure_1[i],
            ex_pressure_2[i],
            ex_flow[i])))

        idx.value = i
        time.sleep(0.005) 

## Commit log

2020-05-02 Initial prototype
2020-05-06 created mock sensor to simulate data
2020-05-07 added pwm control for breathing circuit
2020-05-07 make valve work in mock environment
2020-05-10 New sensors for pressure and flow - LPS35HW for tank and breath pressure - DF6-P0010A2 for flow fronted by ADS1115 ADC
2020-05-11 update mock sensors to handle new sensor types
2020-05-28 enable flow measurement through venturi
2020-06-01 enable 2nd i2c bus and d6f sensor
2020-06-02 update sensor loop to use venturi pressures and composite inspiratory and expiratory flow
2020-06-03 update sensor loop to integrate valve behavior and calculate inspire + expire flow
2020-06-12 Updated sensor state machine to calculate derived metrics Volume, Tidal Volume, and Min Pressure
2020-06-14 breakout sensors into their own files
2020-06-14 add individual sensor files
2020-06-19 flipped a and speaker pin for easier wiring
2020-06-20 support for o2 sensor and syncronization logic change
2020-06-20 support for PEEP stepper
2020-06-20 move o2 sensor it expiry side
2020-06-22 Support for Oxygen Sensor and replacement of Mixing valves with dual breath system
2020-06-24 Updates from round 2 testing
    [VOX_FMEA.xlsx]
2020-06-25 Move sensors and actuators into their own directories and update admin script to include flow calibration
2020-07-28 updated UI section to match pin assignments
2020-08-05 Added BOM csv
    [RevA.csv, RevB.csv]
2020-08-05 fix quoting
    [RevA.csv, RevB.csv]
2020-09-27 Updated part numbers for Tubing and Fitting
    [RevB.csv]
2020-09-27 Updated part numbers
    [RevB.csv]
2020-10-22 Support for DEMO_MODE and L12P motor
2021-04-29 Add debounce to peep valve position feedback The ads sensor was reading back a very bouncy value for the feedback wiper
